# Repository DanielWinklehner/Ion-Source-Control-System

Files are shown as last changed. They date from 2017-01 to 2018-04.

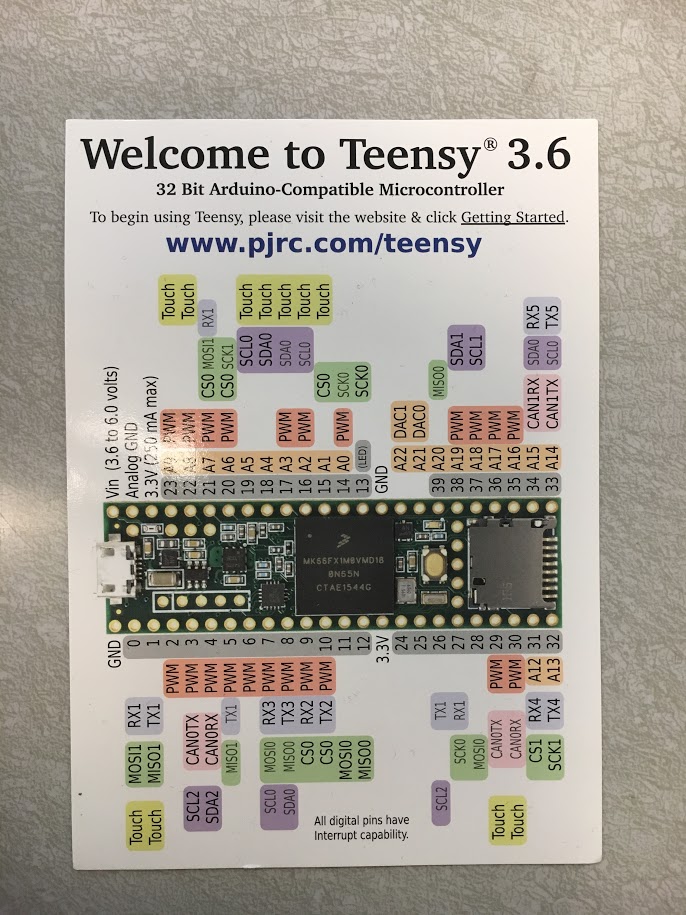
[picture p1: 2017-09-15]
Documents/Manuals/teensy_pinout.JPG

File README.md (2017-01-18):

# Ion Source Control System

## Arduino Error Codes
'ERR0' => Undefined error (does not fall into any of the other 9 categories).
'ERR1' => Asking a precision that's too high (> 6).
'ERR2' => Asking for something that would return more than 128 bytes.
'ERR3' => Invalid number of channels.
'ERR4' => Querying for a channel that does not exist.
'ERR5' => ...
'ERR6' => ...
'ERR7' => ...
...

## Libraries to Install

## Killing the server.

```bash
ps aux | grep RasPiServer.py | grep -v grep | awk '{print $2}' | xargs kill -9 ; python RasPiServer.py 
```

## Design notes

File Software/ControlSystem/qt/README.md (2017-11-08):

# Qt Ion Source Control System Software

Written for Python 3/PyQt5/PyQtGraph

New features:
 - No interruption on device disconnect (requires newest RasPi server)
 - Procedures

Features from the old control system that haven't been implemented:
 - h5 logging

Requirements:
 - Python 3
 - PyQt5
 - PyQtGraph
 - numpy
 - scipy
 - Requests
 - h5py

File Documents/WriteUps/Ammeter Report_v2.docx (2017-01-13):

# Ammeter Report

# Introduction

The main goal of this experiment has been to measure the output signal of a Trans Impedance Amplifier (TIA) wired to a current source. <more information: why are we testing this, what assumptions have you made, what ranges are we interested in? what are all the options for these ranges?>

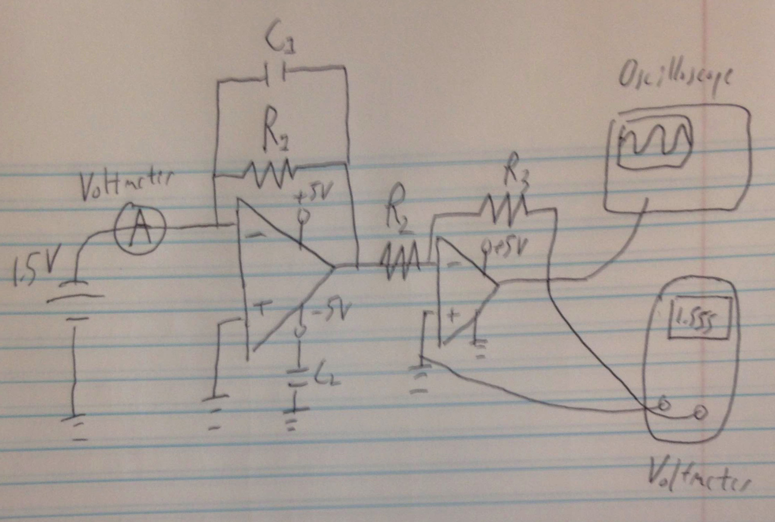
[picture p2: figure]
Macintosh HD:Users:smilner2:Desktop:IMG_0299.pdf

Figure 1: Schematic of the Trans Impedance Amplifier (TIA) with subsequent inverter.

# Setup and Test Cases

The general layout of the circuit is shown in Figure 1.

<restructure and reformat this, explain the parts of the circuit, put all the values in the table instead of the text.>

In this case the current source consisted of a 1.5 V battery connected to a potentiometer that allowed for a wide range of current values. Two different feedback resistors for the TIA were implemented, a 21.9 Ω resistor for a gain 1000 amplifier and a 1.788 k Ω resistor for a gain 10 amplifier. A 1000 μ F feedback capacitor was also incorporated into the TIA as well as another 1000 μ F capacitor which was grounded in order to eliminate noise from the 5V power source.

By conducting measurements using the gain 1000 amplifier it was found that a low feedback resistor corresponds to a very large amount of noise in the range of hundreds of millivolts. Thus it was determined that future measurements using the ammeter should only be done using large feedback resistors with low gain amplification.

Table 1: Resistor and Capacitor values for the different test cases.

Element | Case 1 | Case 2
R1 | 21.9 Ω | 1.788 kΩ
R2
R3
etc….

# Measurements

<brief explanation>

## Case 1

<put everything pertinent to case 1 (21.9 Ohm) here. Table with values, figure, etc.>

## Case 2

<put everything pertinent to case 2 (1.788 kOhm) here. Table with values, figure, etc.>

I(microamps) | V(output) | V(expected) | V(ripple) | Output Error | V(expected)-V(output)
25.6 | 0.549 | 0.553 | 0.002 | 0.00052 | 0.004
31 | 0.662 | 0.67 | 0.0075 | 0.000586 | 0.008
39.5 | 0.848 | 0.865 | 0.01 | 0.000688 | 0.017
46.8 | 1.01 | 1.027 | 0.0066 | 0.000776 | 0.017
53.7 | 1.156 | 1.176 | 0.0056 | 0.000859 | 0.02
67 | 1.465 | 1.467 | 0.0041 | 0.00102 | 0.002
68.3 | 1.472 | 1.475 | 0.0055 | 0.00103 | 0.003
79.8 | 1.722 | 1.724 | 0.0045 | 0.00172 | 0.002
89.4 | 1.933 | 1.931 | 0.0033 | 0.00128 | 0.002
93.1 | 2.013 | 2.011 | 0.0044 | 0.00133 | 0.002
98.5 | 2.126 | 2.128 | 0.0047 | 0.001163 | 0.002
111.1 | 2.401 | 2.399 | 0.0051 | 0.00155 | 0.002
119.9 | 2.599 | 2.59 | 0.0067 | 0.00122 | 0.009
123.9 | 2.683 | 2.676 | 0.0035 | 0.00132 | 0.007
135.6 | 2.918 | 2.929 | 0.013 | 0.00143 | 0.009
148.3 | 3.215 | 3.203 | 0.0088 | 0.00155 | 0.012
158.1 | 3.435 | 3.415 | 0.011 | 0.00176 | 0.03
167.5 | 3.687 | 3.618 | 0.0061 | 0.0019 | 0.069
177.4 | | 3.831 | 0.0072 | 0.0201 | 0
185.6 | | 3.831 | 0.0054 | 0.00222 | 0
196.9 | | 3.831 | 0.003 | 0.00258 | 0

For this case of a 1.785 feedback resistor the data measured included the input current, the output voltage as well as the ripple voltage measured using the oscilloscope. Additional values were the expected output voltage, the difference between expected and output voltages and the error in the expected voltage. The error in the expected voltage was found using Ohm’s law and the intrinsic error in the input current and the resistors. In this case the error in the current was constant at 0.01 μ A and the error in the resistors was also constant at 0.001 k Ω .

After finding the error values for the expected voltage it was possible to add error bars on the graphs in Excel for all the data series that are tabulated above. Using the Custom error option and the Errors data it was possible to add in bars for each data point in the expected output voltage error series.

Table 3. Constant error values

| Output Voltage | Input Current | Resistors
Error | ± 0.01 V | ± 0.01 μA | ± 0.001 k Ω

Figure 4. Table of 21.9 ohm feedback data

I(microamps) | V(ripple) (Volts) | V(Output) (Volts) | V(expected) (Volts) | V(output)-V(expected) (Volts) | Expected Voltage Error
46.9 | 0.23 | 1.416 | 1.027 | 0.389 | 0.000776
68.3 | 0.513 | 1.845 | 1.496 | 0.349 | 0.00111
75.6 | 0.411 | 0.856 | 1.656 | 0.8 | 0.00168
111.6 | 0.354 | 1.999 | 2.444 | 0.445 | 0.00154

# Conclusion

For future work on the ammeter it has been posited that for current values in the 0-200 mA range measuring an output voltage should be done using shunt resistors. The reason for this is due to the high level of noise present in using a low feedback resistor as shown in the data for a 21.9 Ω resistor. For the maximum current of 200 mA in order to achieve a maximum voltage of 3.747 V a shunt resistor of 18.74 Ω should be used which will give a corresponding power of 0.749 W.

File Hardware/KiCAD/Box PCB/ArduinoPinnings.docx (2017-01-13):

Arduino 1

- Solenoid valves
  - Open/closed 1 – 50
  - Open/closed 2 – 52
  - 5v – 46
  - UNUSED – 48 (will flip 4th relay, unconnected)
- Vacuum valves
  - Open 1 – 21
  - Closed 1 – 20
  - Open 2 – 19
  - Closed 2 – 18
- Open LED – 11
- Closed LED – 10
- Error LED – 12
- Com LED – 13

Arduino 2

- Temperature 1
  - SDO – 40
  - SDI – 42
  - SCK – 44
  - CS 1 – 46
  - CS 2 – 48
  - CS 3 – 50
  - CS 4 – 52
- Temperature 2
  - SDO – 53
  - SDI – 51
  - SCK – 49
  - CS 5 – 47
  - CS 6 – 45
  - CS 7 – 43
  - CS 8 – 41
- Flow meters
  - 1 -- 18
  - 2 – 19
  - 3 – 20
  - 4 – 3
  - 5 – 2
- Error LED – 12
- Com LED – 13

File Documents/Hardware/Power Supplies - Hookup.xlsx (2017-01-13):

Label | Volts | Amps | Connect to | Comment
Filament Heating | 200 | 10 | Iso Transformer SEC1
Filament Discharge | 117 | 10 | Iso Transformer SEC2
PLC II | 117 | 1 | Iso Transformer SEC3
Iso Transformer | 208 | 20 | Breaker Box | Breaker Box needs to be made (mushroom shut-off)
Ion Source HV | 240 | 12 | Breaker Box | Runs ok on 208, max 15 A
Einzel Lens HV | 240 | 6 | Breaker Box | Runs ok on 208, max 8 A
Puller | 120 | 5 | Rack Power Strip | Sits in NIM Crate
Turbo Pump Controller | 120 | 8 | Rack Power Strip | 2x
PC | 120 | 5 | Existing Outlets | Nothing to to
PLC I | 120 | 1 | Rack Power Strip
Ion Gauge Controller | 120 | 1 | Rack Power Strip
Interlock Box | 120 | 1 | Rack Power Strip | via extension cord
Roughing Pump | 120 | 8 | Rack Power Strip | via extension cord
Misc | 120 | 5 | Existing Outlets | Nothing to do

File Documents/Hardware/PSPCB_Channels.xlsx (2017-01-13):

For each power supply we will need:
Channel | Value | Description
Remote Voltage Programming | 0-10 V | Arduino supplies 0-10V to remotely set voltage of PS (0-5V mode with jumper)
Remote Current Programming | 0-10 V | Arduino supplies 0-10V to remotely set current of PS (0-5V and 0-100mV modes with jumpers)
Remote Voltage Feedback | 0-10 V | Arduino reads 0-10V to remotely read voltage of PS (0-5V mode with jumper)
Remote Current Feedback | 0-10 V | Arduino reads 0-10V to remotely read current of PS (0-5V mode with jumper)
Remote Current Feedback 2 | 0-100mV | Gets dedicated channel as it will need an op-amp
Close PS Interlock | 0/1 | Closes/opens a contact to allow/inhibit PS output. Maybe a relay?
PS ON/OFF Passive | 0/1 | Closes/opens a contact to switch on/off PS. Maybe a relay?
PS ON/OFF Active | 0/10V | Put Output to HIGH (10V)/LOW (0V) to switch on/off PS
External Interlock Input | 0/1 | Register if an external wire loop is closed or not. Connect to Arduino interrupt.
HV ON/OFF Indicator |  | Active Transistor. Maximum output current is 30mA via an output resistance of 440R
Trip Indicator |  | Active Transistor. Maximum output current is 30mA via an output resistance of 440R
Local/Remote Indicator |  | Active Transistor. Maximum output current is 30mA via an output resistance of 440R
Arc Monitor Status Indicator |  | Active Transistor. Maximum output current is 30mA via an output resistance of 440R
V Status Indicator |  | Active Transistor. Maximum output current is 30mA via an output resistance of 440R
I Status Indicator |  | Active Transistor. Maximum output current is 30mA via an output resistance of 440R
In addition, each arduino gets:
Communicating LED
Error State LED
Reset Button
Highly stable reference voltage
Other ideas?

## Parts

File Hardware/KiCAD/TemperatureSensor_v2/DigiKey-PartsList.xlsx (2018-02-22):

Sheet: First Order
name | part number | qty
100 nF cap | 490-6328-1-ND | 22
10 uF cap | 490-10693-1-ND | 1
diode | 1N4148WXTPMSTR-ND | 6
led | 160-1447-2-ND | 4
zener | BZT52C15-FDITR-ND | 1
fuse holder | F1498-ND | 1
barrel jack | CP-202B-ND | 1
com connector | S7002-ND | 1
3.3k resistor | RR08P3.3KDCT-ND | 6
1k resistor | RR05P1.0KDCT-ND | 4
push button | EG2509-ND | 1
voltage regulator | 497-1491-5-ND | 1

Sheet: Revision
name | part number | qty
100 nF cap | 709-1183-1-ND | 22
10 uF cap | 490-10693-1-ND | 1
diode | 1N4148WXTPMSTR-ND | 6
led | 160-1447-2-ND | 4
zener | BZT52C15S-FDICT-ND | 1
fuse holder | 486-2019-ND | 2
barrel jack | CP-202AH-ND | 1
com connector | S7002-ND | 1
3.3k resistor | P3.3KDBCT-ND | 6
1k resistor | RR08P1.0KDDKR-ND | 4
push button | EG2509-ND | 1
voltage regulator | 497-1491-5-ND | 1
MAX | MAX31856MUD+-ND | 1

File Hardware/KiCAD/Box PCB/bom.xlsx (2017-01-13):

Component | Value | Quantity | size/ref
Capacitor
 | 10uF | 1 | 805 | http://www.mouser.com/ProductDetail/TDK/C2012X7R1A106K125AE/
 | .1uF | 25 | 805 | http://www.mouser.com/ProductDetail/Vishay-Vitramon/VJ0805Y104JXQCW1BC/
 | .01uF | 16 | 805 | http://www.mouser.com/ProductDetail/Vishay-Vitramon/VJ0805Y103JXQCW1BC/
Resistor
 | 1k | 14 | 603 | http://www.mouser.com/ProductDetail/Bourns/CRT0603-BY-1001EAS/
 | 3.3k | 12 | 603 | http://www.mouser.com/ProductDetail/Panasonic/ERA-3AEB332V/
 | 10k | 7 | 603 | http://www.mouser.com/ProductDetail/Bourns/CRT0603-BY-1002EAS/
Diode |  | 10
 | n/a |  | SMD SOD-323 | http://www.mouser.com/ProductDetail/Vishay-Semiconductors/1N4148WS-E3-08/?qs=sGAEpiMZZMtoHjESLttvkjs26zymxl2FcQ6lZ9nzG2I%3d
LED
 | red | 8 | 3mm | http://www.mouser.com/ProductDetail/Kingbright/WP710A10ID/
transistor |  | 2 | SOT-223 | http://www.mouser.com/Search/ProductDetail.aspx?qs=UMEuL5FsraAkzKOnvvq6XA%3d%3d
voltage regulator |  | 1 | SOT-223-3 | http://www.mouser.com/ProductDetail/STMicroelectronics/LD1117S33TR/?qs=edoyzKMbmhntQZx4BFmoqw%3D%3D
Connectors
 | 01x02 | 9
 | 01x07 | 2
 | 01x09 | 1
 | 01x13 | 4
MAX31856
 |  | 8 | 14 pin TSSOP | http://www.mouser.com/ProductDetail/Maxim-Integrated/MAX31856MUD+/
Solder paste
 | Easy 256 from Kester
Solder squeegee

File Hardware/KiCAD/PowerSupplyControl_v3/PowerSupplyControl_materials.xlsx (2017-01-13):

Item | value | Quantity (per board) | Footprint | Link
Diode
 |  | 4 | SOD-323 | http://www.mouser.com/ProductDetail/Vishay-Semiconductors/1N4148WS-E3-08/?qs=sGAEpiMZZMtoHjESLttvkjs26zymxl2FcQ6lZ9nzG2I%3d
Resistors
 | 1k | 42 | 603 | http://www.mouser.com/ProductDetail/Bourns/CRT0603-BY-1001EAS/
 | 1.4k | 4 | 603 | http://www.mouser.com/ProductDetail/Panasonic/ERA-3AEB1401V/
 | 3.3k | 8 | 603 | http://www.mouser.com/ProductDetail/Panasonic/ERA-3AEB332V/?qs=sGAEpiMZZMu61qfTUdNhGxEjuuBLd0B4AgtkKscHp9I%3d
 | 10k | 5 | 603 | http://www.mouser.com/ProductDetail/ARCOL-Ohmite/APC0603B10K0N/
 | 13k | 8 | 603 | http://www.mouser.com/ProductDetail/Susumu/RR0816P-133-D/
 | 20k | 12 | 603 | http://www.mouser.com/ProductDetail/ARCOL-Ohmite/APC0603B20K0N/
 | 487k | 4 | 805 | http://www.mouser.com/ProductDetail/Welwyn-Components-TT-Electronics/PCF0805R-487KBT1/
Capacitors
 | 0.01uF | 4 | 805 | http://www.mouser.com/ProductDetail/Murata-Electronics/GRM2195C1H103FA01D/?qs=sGAEpiMZZMs0AnBnWHyRQG5q9snugj0Qdwer2IwkegU%3d
 | 0.1uF | 9 | 805 | http://www.mouser.com/ProductDetail/Kemet/C0805C104J5RACTU/
 | 1uF | 1 | 805 | http://www.mouser.com/ProductDetail/Kemet/C0805C105J4RACTU/
 | 10uF | 1 | 805 | http://www.mouser.com/ProductDetail/Murata-Electronics/GRM21BR61C106KE15L/?qs=sGAEpiMZZMs0AnBnWHyRQFQYdTDrJniY6UiV3hUxNOg%3d
 | 47uF | 4 | 1210 | http://www.mouser.com/ProductDetail/Murata-Electronics/GRM32EC81C476KE15L/
DIP switches
 |  | 4 |  | http://www.mouser.com/ProductDetail/CK-Components/BD01/?qs=mh%2FGhdZp9qW9ttlbghPYvg%3D%3D
MAX31856
 |  | 2 |  | http://www.mouser.com/ProductDetail/Maxim-Integrated/MAX31856MUD+/
Terminal Blocks
 |  | 3 (2 pole)
 |  | 3 (10 pole)
Double sided headers
 |  | 1 (6 pins) | 2.54mm | http://www.mouser.com/ProductDetail/SchmartBoard/920-0085-01/
 |  | 5 (8 pins) | 2.54mm | http://www.mouser.com/ProductDetail/SchmartBoard/920-0086-01/
 |  | 1 (2x18 pins) | 2.54mm | http://www.mouser.com/ProductDetail/SchmartBoard/920-0103-01/
 |  | ~~(maybe extenders?)~~ | ~~2.54mm~~
Op Amps
 |  | 3 | soic-14 | http://www.mouser.com/ProductDetail/Texas-Instruments/LM324MX-NOPB/
ADR4550
 |  | 1 |  | http://www.mouser.com/ProductDetail/Analog-Devices/ADR4550BRZ/?qs=sGAEpiMZZMv9Q1JI0Mo%2ftYZUeGvTlaqP

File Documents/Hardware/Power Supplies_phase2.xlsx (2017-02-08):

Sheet: Sheet1
Description | Company | Series | Input | Phases | Max Output | Max Power | Iso Transformer | Comment
Filament Current Supply | Electronic Measurements, Inc. | TCR | 190-250 VAC | 1 | 10 VDC, 300 A | 1.2 kW | SEC1 | Not going to exceed 100 A, Set PLC upper limit.
Filament Discharge Supply | Power Ten, Inc. | 3300P | 120 VAC | 1 | 100 VDC, 10A | 1.2 kW | SEC2
PLC II | MIT | - | 120 VAC | 1 | - | 500 W | SEC3 | PLC II for everything on HV potential
Isolation Transformer | Stewart Transformers, London | STL | 208 VAC | 1 | - | 4 kVA | PRY | See Plaque for Output, 60 kV isolation
HV Power Supply | Farnell Hivolt | 2500 | 240 VAC | 1 | 20 kV, 120 mA | 2.9 kW | N/A | Runs OK on 208 VAC
Einzel Lens Power Supply | Glassman High Voltage, Inc. | WX | 240 VAC | 1 | 30 kV, 40 mA | 1.4 kW | N/A | 2 phases from 120/208 VAC?
Extraction, Negative PS | TBD | TBD | 120 VAC | 1 | 5 kV, 40 mA | 300 W | N/A | Need to buy this, necessary in MIST-1/Phase II
Turbo Pump Controller | ? | ? | 120 VAC | 1 | - | ? | N/A | Will eventually run 2 of them
PC | - | - | 120 VAC | 1 | - | 500 W | N/A
PLC I | MIT | - | 120 VAC | 1 | - | 500 W | N/A | PLC I for everything not on HV potential
Ion Gauge Controller | MIT | - | 120 VAC | 1 | - | 150 W | N/A
Misc | MIT | - | 120 VAC | 1 | - | 1 kW | N/A | Other diagnostic devices, not to exceed 1 kW
On HV Potential
Iso Transformer
On Ground Potential

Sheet: Sheet2
Label | Volts | Amps | Connect to | Comment
Filament Heating | 200 | 10 | Iso Transformer SEC1
Filament Discharge | 117 | 10 | Iso Transformer SEC2
PLC II | 117 | 1 | Iso Transformer SEC3
Iso Transformer | 208 | 20 | Breaker Box | Breaker Box needs to be made (mushroom shut-off)
Ion Source HV | 240 | 12 | Breaker Box | Runs ok on 208
Einzel Lens HV | 240 | 6 | Breaker Box | Runs ok on 208
Puller | 120 | 5 | Rack Power Strip | Sits in NIM Crate
Turbo Pump Controller | 120 | 8 | Rack Power Strip | 2x
PC | 120 | 5 | Existing Outlets | Nothing to to
PLC I | 120 | 1 | Rack Power Strip
Ion Gauge Controller | 120 | 1 | Rack Power Strip
Interlock Box | 120 | 1 | Rack Power Strip
Misc | 120 | 5 | Existing Outlets | Nothing to do
Dipole PS | 120 | 20
Quad PS | 120 | 20 |  | 2x
Lines: |  |  |  |  | Watts
1 | 208 | 20 | to Transformer | shunt-tripped | 4160
2 | 208 | 16 | to HV 1 | shunt-tripped | 3328
3 | 208 | 16 | to HV 2 | shunt-tripped | 3328
4 | 120 | 16 | Rack Strip 1 | shunt-tripped | 1920
5 | 120 | 16 | Rack Strip 2 |  | 1920
6 | 120 | 20 | Dipole PS |  | 2400
7 | 120 | 20 | Quad PS 1 |  | 2400
8 | 120 | 20 | Quad PS 2 |  | 2400
9 | 120 | 16 | Misc 1 | Existing wall strips | 1920
10 | 120 | 16 | Misc 2 | Existing wall strips | 1920
 |  |  |  |  | 25.7 | kW

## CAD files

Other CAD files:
Hardware/KiCAD/TemperatureSensor/inventor/temp_sensor_front_plate.dwg
Hardware/KiCAD/TemperatureSensor/inventor/temp_sensor_back_plate.ipt
Hardware/KiCAD/TemperatureSensor/inventor/temp_sensor_front_plate.ipt

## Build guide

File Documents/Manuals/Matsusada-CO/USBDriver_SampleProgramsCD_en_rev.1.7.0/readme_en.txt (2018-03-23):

====================================================================================================
[Software ]		USB Driver / Sample Programs
[ Version ]		Ver.1.7.0
[Copyright]		2016(c) Matsusada Precision Inc, All rights reserved.
[  U R L  ]		www.matsusada.com/
====================================================================================================

1. About "USB Driver / Sample Programs"
	"USB Driver / Sample Programs" contains drivers, manuals and sample programs to control
	the USB devices made by Matsusada Precision Inc.
	You should install this driver in the operating environment to control the USB devices
	made by Matsusada Precision Inc. remotely.

2. Directory Structure
	"USBDriver_SamplePrograms"
		„° "readme_en.txt"
		„° "Documents"
		„«		„° "CDM 2 08 28 Release Info.rtf"			�F	Driver Rev.2.08.28 Release Info
		„«		„° "D2XX_Programmer's_Guide(FT_000071).pdf"	�F	Device Driver Programmer's Guide (English)
		„«		„° "LogoVerificationReport.pdf"				�F	Windows Certification Report
		„«		„¯ "USBDriverInstallationGuide_en_rev.1.3.pdf"	�F	USB Driver Installation Guide (English)
		„° "Drivers"										�F	Device Driver Set
		„¯ "Sample Programs"
				„° "LabVIEW"								�F	Sample Program for LabVIEW
				„° "VB"										�F	Sample Program for VB
				„° "VC#"									�F	Sample Program for VC#
				„° "VC++"									�F	Sample Program for VC++
				„¯ "Matsusada_USB_Check.exe"				�F	Communication Check Program

3. Corresponded OS
	Windows 10(32/64bit)(*), 8.1(32/64bit)(*), 8(32/64bit), 7(32/64bit), VISTA(32/64bit), XP(32/64bit)(**)
	(*)	It does not officially get certified with Windows 10 and 8.1 by Microsoft Inc,
		but it was confirmed the operation at Matsusada Precision Inc.
	(**)Operation on Windows XP has been confirmed by us.
		But we preclude any possibility of support for operation on Windows XP, as Support
		for it by Microsoft is terminated.

4. Driver Installation
	Refer to attached "USBDriverInstallationGuide_en_rev.1.3.pdf", install the driver.

5. Exemption Clause
	We are not responsible at all for any trouble or damage, even if such a trouble or damage
	should have happened about your PC, peripheral units, and/or data.  You are requested to
	understand this clause before using the software.

6. Copyright
	The copyright related to this software is possessed by Matsusada Precision Inc.

[EOF]

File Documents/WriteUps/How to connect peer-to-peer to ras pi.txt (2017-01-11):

The Raspberry Pi needs to have a static IP set on it. For this document, let's assume it's 10.77.0.3

On your computer:

1) Disable WiFi
2) Set up static IP for your computer as well. Set it to: 10.77.0.1. Set the netmask to 255.255.0.0 and the gateway to 10.77.0.1 (or whatever static IP you have set your computer's address to).
3) Ping the IP of the Pi to see if it responds.
4) SSH.

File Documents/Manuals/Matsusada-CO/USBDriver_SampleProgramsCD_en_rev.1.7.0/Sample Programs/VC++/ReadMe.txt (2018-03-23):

========================================================================
    アプリケーション: Matsusada_USB_Sample プロジェクトの概要
========================================================================

この Matsusada_USB_Sample アプリケーションは、AppWizard により作成されました。  

このファイルには、Matsusada_USB_Sample 
アプリケーションを構成する各ファイルの内容の概要が含まれています。

Matsusada_USB_Sample_Cpp.vcxproj
    これは、アプリケーション ウィザードを使用して生成された VC++ 
    プロジェクトのメイン プロジェクト ファイルです。 
    ファイルを生成した Visual C++ のバージョンに関する情報と、アプリケーション 
    ウィザードで選択されたプラットフォーム、
    構成、およびプロジェクト機能に関する情報が含まれています。

Matsusada_USB_Sample_Cpp.vcxproj.filters
    これは、アプリケーション ウィザードで生成された VC++ プロジェクトのフィルター 
    ファイルです。 
    このファイルには、プロジェクト内のファイルとフィルターとの間の関連付けに関する
    情報が含まれています。 
    この関連付けは、特定のノードで同様の拡張子を持つファイルのグループ化を
    示すために IDE で使用されます (たとえば、".cpp" ファイルは "ソース ファイル" 
    フィルターに関連付けられています)。

Matsusada_USB_Sample.cpp
    これは、メインのアプリケーション ソース ファイルです。
    フォームを表示するコードが含まれています。

Matsusada_USB_Sample.h
    フォーム クラスと InitializeComponent() 関数の実装が含まれています。

AssemblyInfo.cpp
    アセンブリ メタデータを変更するカスタム属性が含まれています。

/////////////////////////////////////////////////////////////////////////////
その他の標準ファイル :

StdAfx.h、StdAfx.cpp
    これらのファイルは、Matsusada_USB_Sample_Cpp.pch 
    という名前のプリコンパイル済みヘッダー (PCH) ファイルと、StdAfx.obj 
    という名前のプリコンパイル済みの型ファイルを構築するために使用されます。

/////////////////////////////////////////////////////////////////////////////

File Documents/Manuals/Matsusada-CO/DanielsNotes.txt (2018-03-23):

1. Manually install d2xx drivers on RasPi. Has to be version 1.3.x (or maybe just have to sudo).
Link: http://www.ftdichip.com/Drivers/D2XX.htm (use the v6 that says works on RasPi, follow instructions in readme in the rightmost column)
(CO-U32 serial number is CO001144)
2. If you compile the tests/examples, there is a small modification necessary in the loopback example 
(just add "../" in front of the import statement in main.c)
3. Install ftd2xx from https://github.com/ctrl-shift-esc/ftd2xx (has Linux version as opposed to PyUSB 1.6)
4. Compile ftd2xx as sudo! (sudo python setup.py install)

5. Run python as sudo, test the comunication:

BaudRate 9600, 8 data bits, 1 stop bit, no parity, no flow control
500 ms read, 100 ms write timeout (in Matsusada Example Code)

import ftd2xx

ftd2xx.setVIDPID(0x1192, 0x1000)  # Add our devices Vendor ID and Product ID to the loaded list of FTDI ID's
dev = ftd2xx.open(0)  # if there is only one FTDI device connected or CO happens to be the first one in the list, otherwise, different index
dev.setBaudRate(9600)
dev.setDataCharacteristics(8, 0, 0)  # 8 data bits, 1 stop bit (for some reason BITS_8 = 0), parity none = 0
dev.setFlowControl(0x0000)
dev.write("#1 REN\r")  # needs a carriage return, not a newline! #1 can be replaced with units 2, 3, 4, etc.

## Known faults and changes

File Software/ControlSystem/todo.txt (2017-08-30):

Procedures

 - User can define procedures, with access to channels
    e.g. "if channel goes over this value, do X"
 - Idea: Drop down combobox w/ channels, put in max/min values
 - Idea: Pop up screen with active channels and variable names, example script, user writes simple if statements

Error Handling

 - Between raspberry pi and gui, between raspberry pi and devices
    currently sends back ERR[0-9]
 - Timeouts between GUI and raspberry pi, if arduino goes offline
    Displaying polling rate in GUI, falls back to polling rate of slowest arduino

General

 - Front page overview, can set overview present when channel is created
 - Decide which panels we want on the front page, currently everything is on the front page
 - Python3 ready
 - Move to QT?

USB

 - Driver for new power supply

Arduino

 - Arduino IDE installed, go to libraries folder, create a folder for the communications library
    Create a symlink to libraries folder
 - Test Arduino using serial plotter from Arduino IDE
 - Has a function for querying value of specific channel, and listing channels available
    sends 'i' or 'c', sends back list of channel names, use to determine which channels to fill

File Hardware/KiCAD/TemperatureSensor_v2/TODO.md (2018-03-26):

# Temperature Sensor (v2) Todo Items

Author: Thomas Wester

Email: twester@mit.edu

Date: 2018/03/06

 - The Arduino footprint is slightly too wide. This
   should be narrowed by ~0.5 mm.

 - Test pads should be added around each MAX controller
   and probably the voltage regulator.

 - The labelling can be improved. The capacitors and MAXs
   have difficult-to-follow numberings. The SDO pin is
   missing a label.

 - The thermocouple footprint pads are too close together.
   These should be extended by ~0.5mm.

 - The solder pads for the thermocouple connectors are too
   small. These should be extended by ~0.5mm.

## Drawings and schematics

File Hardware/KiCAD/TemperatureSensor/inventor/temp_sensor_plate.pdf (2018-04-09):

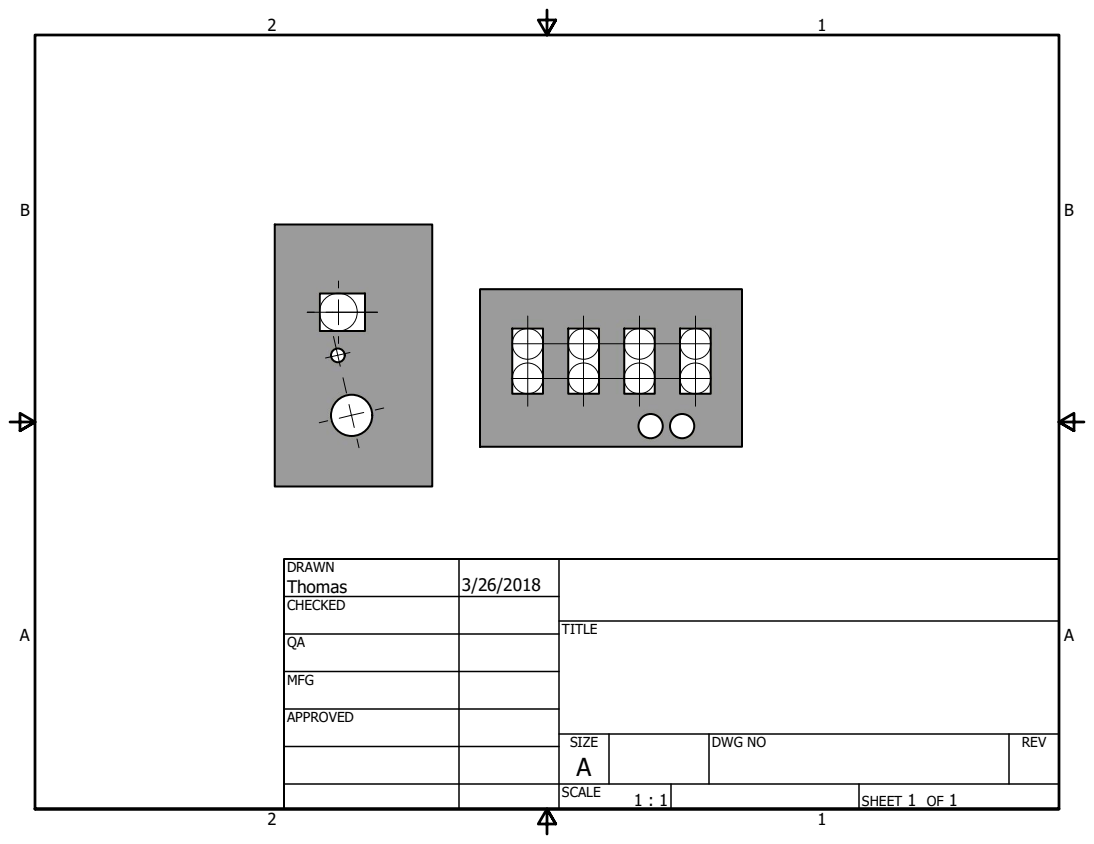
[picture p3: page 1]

DRAWN Thomas | 3/26/2018

CHECKED

MFG

APPROVED

SIZE A | DWG NO | REV

SCALE 1 : 1 | | SHEET 1 OF 1

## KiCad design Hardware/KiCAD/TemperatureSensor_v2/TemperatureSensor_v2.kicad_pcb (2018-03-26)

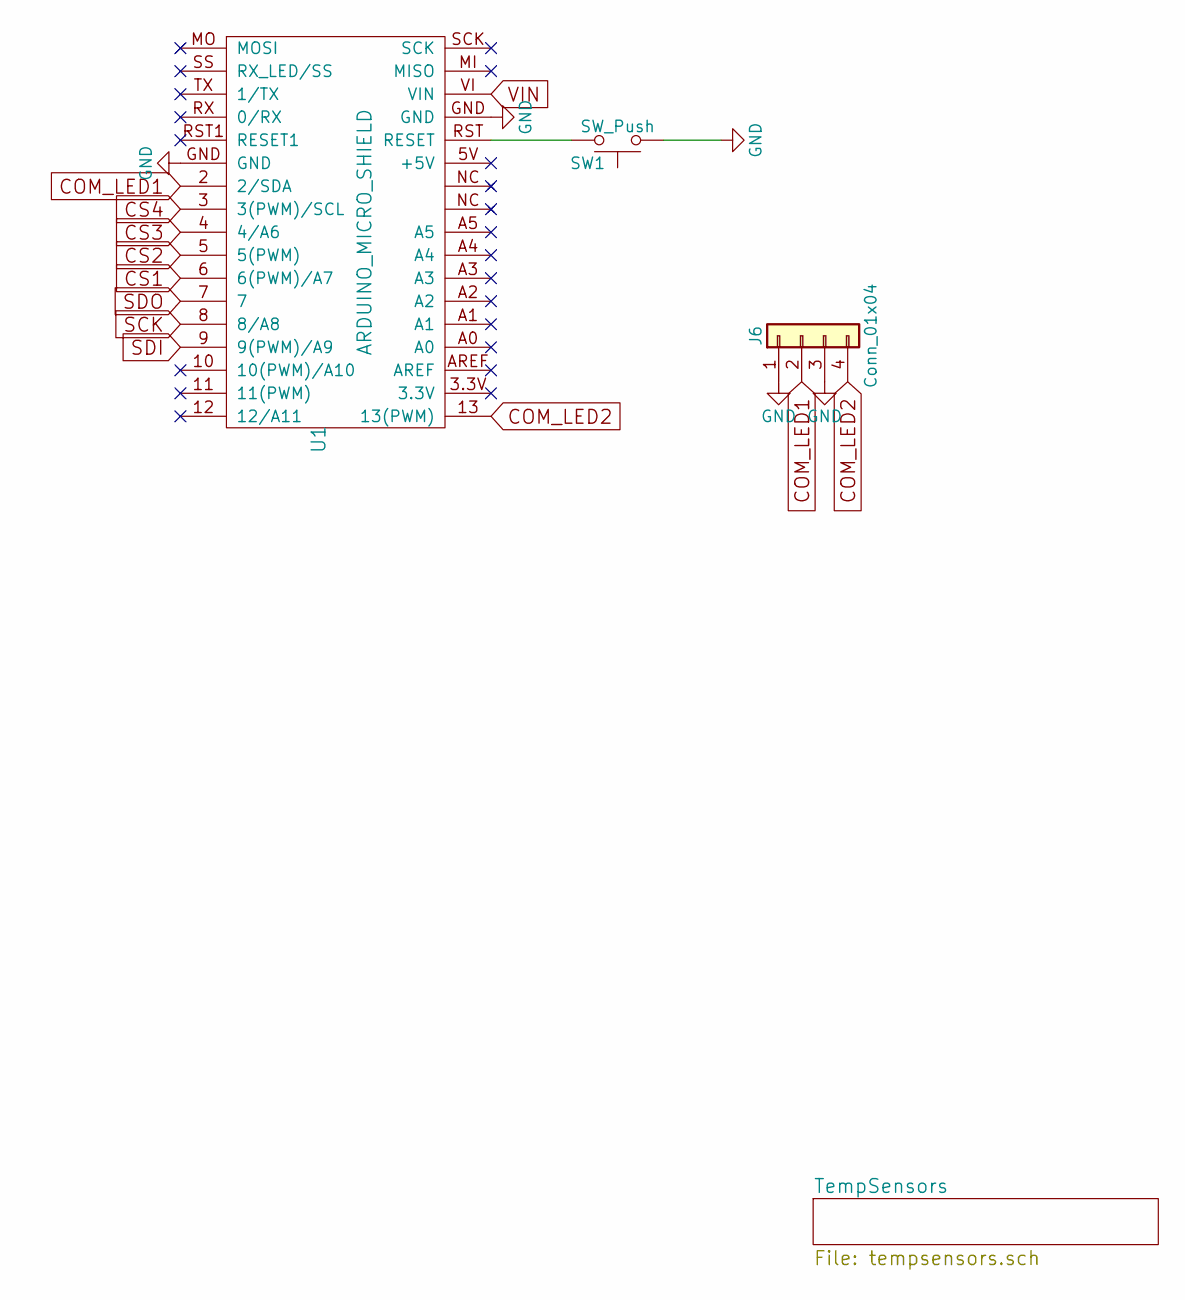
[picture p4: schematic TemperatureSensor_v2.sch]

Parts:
J6: Conn_01x04; TerminalBlock_Phoenix_MPT-2.54mm_4pol
SW1: SW_Push; SW_Tactile_SPST_Angled_PTS645Vx39-2LFS
U1: ARDUINO_MICRO_SHIELD; ARDUINO_MICRO_SHIELD1

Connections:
COM_LED1: J6.2, U1.2 (2/SDA)
COM_LED2: J6.4, U1.13 (13(PWM))
CS1: U1.6 (6(PWM)/A7); also elsewhere on the board
CS2: U1.5 (5(PWM)); also elsewhere on the board
CS3: U1.4 (4/A6); also elsewhere on the board
CS4: U1.3 (3(PWM)/SCL); also elsewhere on the board
GND: J6.1, J6.3, SW1.1, U1.GND; also elsewhere on the board
unnamed: SW1.2, U1.RST (RESET)
SCK: U1.8 (8/A8); also elsewhere on the board
SDI: U1.9 (9(PWM)/A9); also elsewhere on the board
SDO: U1.7; also elsewhere on the board
VIN: U1.VI (VIN); also elsewhere on the board

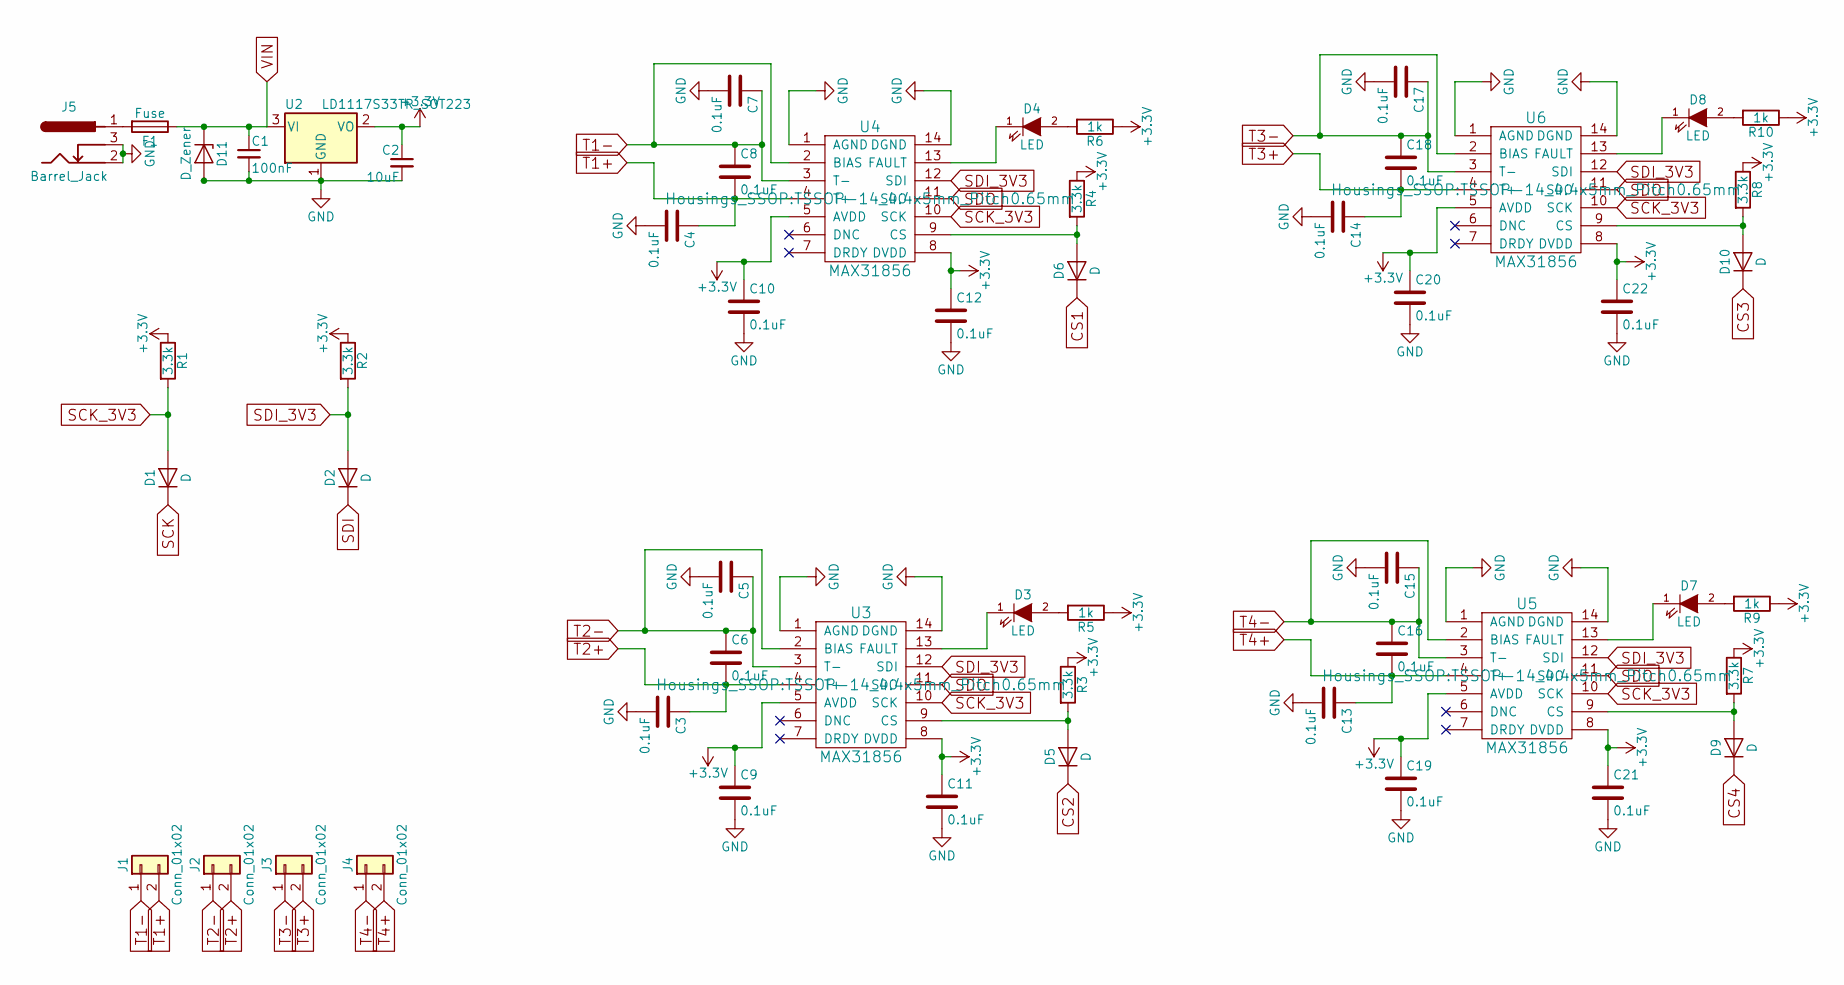
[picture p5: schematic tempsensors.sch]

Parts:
C1: 100nF; C_0805
C2: 10uF; C_0805
C3, C4, C5, C6, C7, C8, C9, C10, C11, C12, C13, C14, C15, C16, C17, C18, C19, C20, C21, C22: 0.1uF; C_0805
D1, D2, D5, D6, D9, D10: D; D_SOD-323
D3, D4, D7, D8: LED; LED_0603
D11: D_Zener; D_0805
F1: Fuse; Fuseholder5x20_horiz_open_inline_Type-I
J1, J2, J3, J4: Conn_01x02; Thermocouple_Pins
J5: Barrel_Jack; BARREL_JACK
R1, R2, R3, R4, R7, R8: 3.3k; R_0603
R5, R6, R9, R10: 1k; R_0603
U2: LD1117S33TR_SOT223; TO-220-3_Vertical
U3, U4, U5, U6: MAX31856; TSSOP-14_4.4x5mm_Pitch0.65mm

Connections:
+3V3: C2.1, C9.1, C10.1, C11.1, C12.1, C19.1, C20.1, C21.1, C22.1, R1.1, R2.1, R3.1, R4.1, R5.1, R6.1, R7.1, R8.1, R9.1, R10.1, U2.2 (VO), U3.5 (AVDD), U3.8 (DVDD), U4.5 (AVDD), U4.8 (DVDD), U5.5 (AVDD), U5.8 (DVDD), U6.5 (AVDD), U6.8 (DVDD)
CS1: D6.1 (K); also elsewhere on the board
CS2: D5.1 (K); also elsewhere on the board
CS3: D10.1 (K); also elsewhere on the board
CS4: D9.1 (K); also elsewhere on the board
GND: C1.2, C2.2, C3.2, C4.2, C5.2, C7.2, C9.2, C10.2, C11.2, C12.2, C13.2, C14.2, C15.2, C17.2, C19.2, C20.2, C21.2, C22.2, D11.2 (A), J5.2, J5.3, U2.1 (GND), U3.1 (AGND), U3.14 (DGND), U4.1 (AGND), U4.14 (DGND), U5.1 (AGND), U5.14 (DGND), U6.1 (AGND), U6.14 (DGND); also elsewhere on the board
unnamed: D3.1 (K), U3.13 (FAULT)
unnamed: D3.2 (A), R5.2
unnamed: D4.1 (K), U4.13 (FAULT)
unnamed: D4.2 (A), R6.2
unnamed: D5.2 (A), R3.2, U3.9 (CS)
unnamed: D6.2 (A), R4.2, U4.9 (CS)
unnamed: D7.1 (K), U5.13 (FAULT)
unnamed: D7.2 (A), R9.2
unnamed: D8.1 (K), U6.13 (FAULT)
unnamed: D8.2 (A), R10.2
unnamed: D9.2 (A), R7.2, U5.9 (CS)
unnamed: D10.2 (A), R8.2, U6.9 (CS)
unnamed: F1.2, J5.1
SCK: D1.1 (K); also elsewhere on the board
SCK_3V3: D1.2 (A), R1.2, U3.10 (SCK), U4.10 (SCK), U5.10 (SCK), U6.10 (SCK)
SDI: D2.1 (K); also elsewhere on the board
SDI_3V3: D2.2 (A), R2.2, U3.12 (SDI), U4.12 (SDI), U5.12 (SDI), U6.12 (SDI)
SDO: U3.11 (SDO), U4.11 (SDO), U5.11 (SDO), U6.11 (SDO); also elsewhere on the board
T1+: C4.1, C8.2, J1.2, U4.4 (T+)
T1-: C7.1, C8.1, J1.1, U4.2 (BIAS), U4.3 (T-)
T2+: C3.1, C6.2, J2.2, U3.4 (T+)
T2-: C5.1, C6.1, J2.1, U3.2 (BIAS), U3.3 (T-)
T3+: C14.1, C18.2, J3.2, U6.4 (T+)
T3-: C17.1, C18.1, J3.1, U6.2 (BIAS), U6.3 (T-)
T4+: C13.1, C16.2, J4.2, U5.4 (T+)
T4-: C15.1, C16.1, J4.1, U5.2 (BIAS), U5.3 (T-)
VIN: C1.1, D11.1 (K), F1.1, U2.3 (VI); also elsewhere on the board

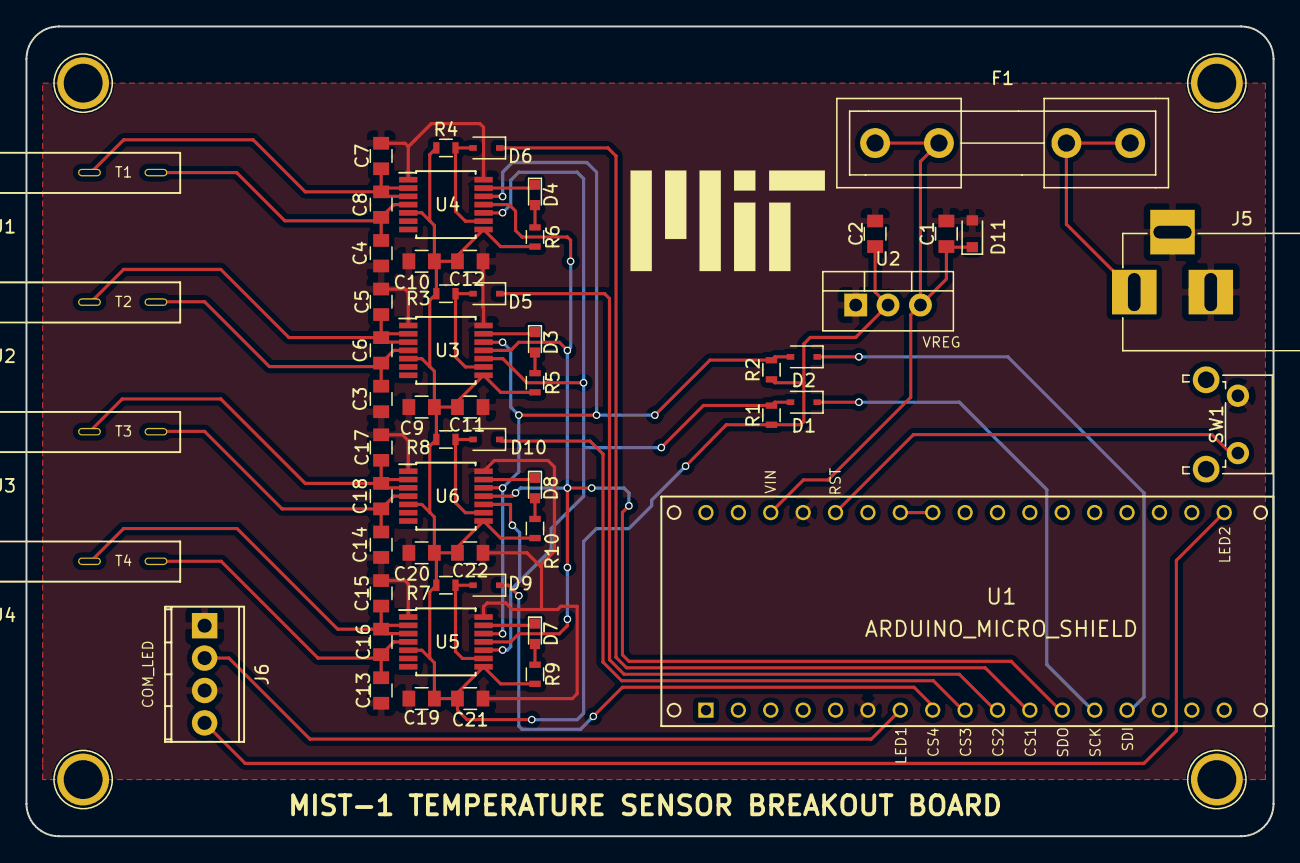
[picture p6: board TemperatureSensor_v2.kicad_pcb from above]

Board: 2 copper layers, 97.8 x 63.5 mm, 57 parts (0 on the bottom side), 36 nets.

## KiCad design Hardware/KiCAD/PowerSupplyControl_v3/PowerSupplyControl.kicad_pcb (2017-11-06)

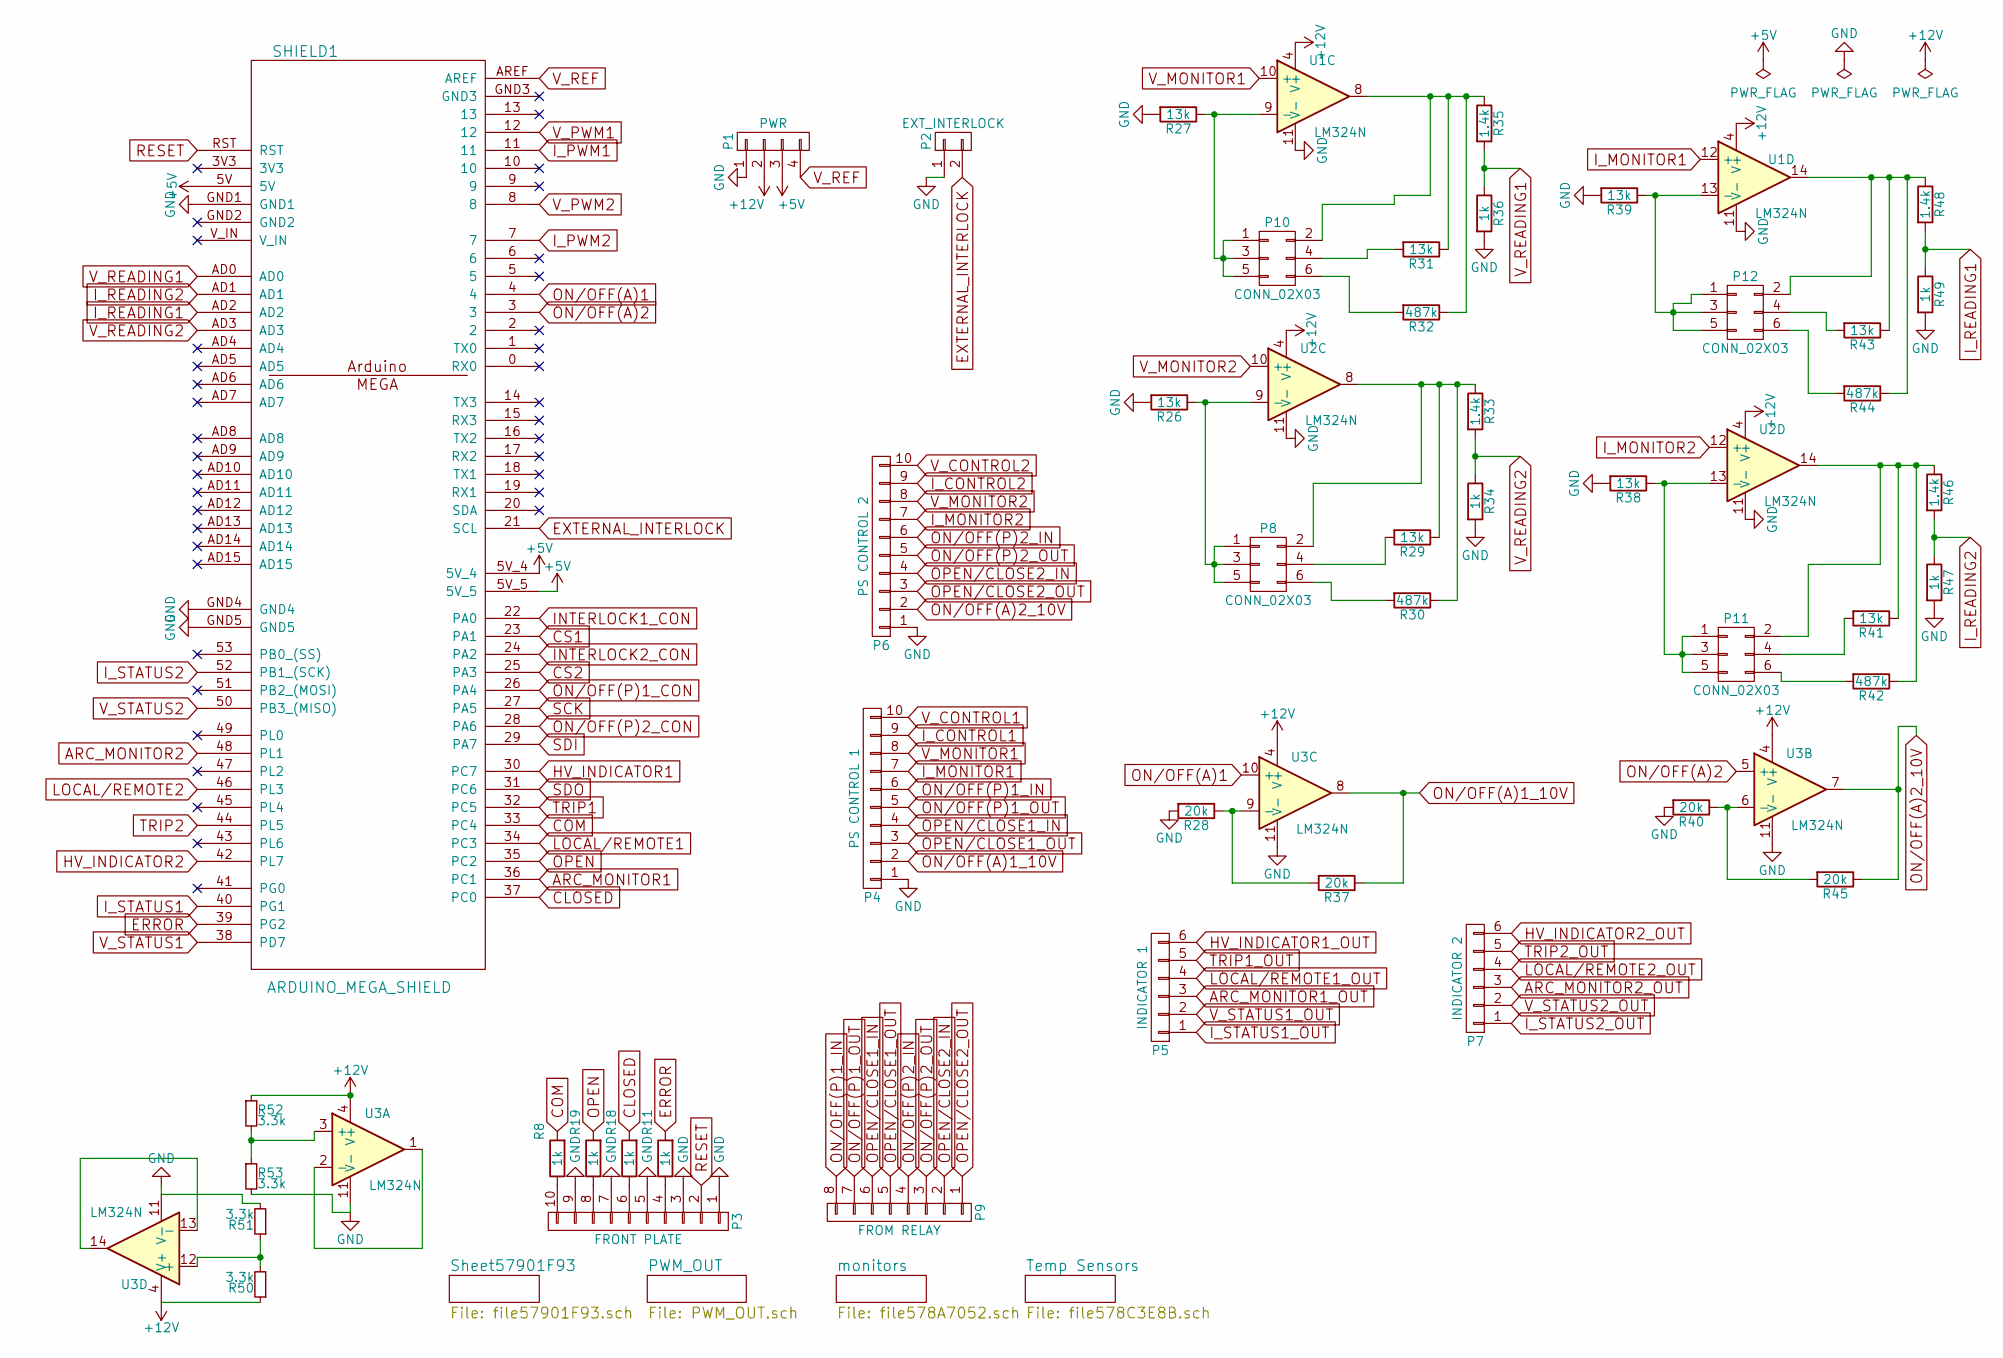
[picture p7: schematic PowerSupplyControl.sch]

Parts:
P1: PWR; Pin_Header_Straight_1x04
P2: EXT_INTERLOCK; TerminalBlock_Pheonix_PT-3.5mm_2pol
P3: FRONT PLATE; TerminalBlock_Pheonix_PT-3.5mm_10pol
P4: PS CONTROL 1; TerminalBlock_Pheonix_PT-3.5mm_10pol
P5: INDICATOR 1; Pin_Header_Straight_1x06
P6: PS CONTROL 2; TerminalBlock_Pheonix_PT-3.5mm_10pol
P7: INDICATOR 2; Pin_Header_Straight_1x06
P8, P10, P11, P12: CONN_02X03; Pin_Header_Straight_2x03
P9: FROM RELAY; Pin_Header_Straight_1x08
R8, R11, R18, R19, R34, R36, R47, R49: 1k; R_0603
R26, R27, R29, R31, R38, R39, R41, R43: 13k; R_0603
R28, R37, R40, R45: 20k; R_0603
R30, R32, R42, R44: 487k; R_0805
R33, R35, R46, R48: 1.4k; R_0603
R50, R51, R52, R53: 3.3k; R_0603
SHIELD1: ARDUINO_MEGA_SHIELD
U1, U2, U3: LM324N; SOIC-14_N

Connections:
+5V: P1.3, SHIELD1.5V, SHIELD1.5V_4, SHIELD1.5V_5; also elsewhere on the board
+12V: P1.2, R50.1, R52.1, U1.4 (V+), U2.4 (V+), U3.4 (V+)
ARC_MONITOR1: SHIELD1.36 (PC1); also elsewhere on the board
ARC_MONITOR1_OUT: P5.3; also elsewhere on the board
ARC_MONITOR2: SHIELD1.48 (PL1); also elsewhere on the board
ARC_MONITOR2_OUT: P7.3; also elsewhere on the board
CLOSED: R18.2, SHIELD1.37 (PC0)
COM: R8.2, SHIELD1.33 (PC4)
CS1: SHIELD1.23 (PA1); also elsewhere on the board
CS2: SHIELD1.25 (PA3); also elsewhere on the board
ERROR: R11.2, SHIELD1.39 (PG2)
EXTERNAL_INTERLOCK: P2.2, SHIELD1.21 (SCL)
GND: P1.1, P2.1, P3.1, P3.3, P3.5, P3.7, P3.9, P4.1, P6.1, R26.2, R27.2, R28.2, R34.2, R36.2, R38.2, R39.2, R40.2, R47.2, R49.2, R51.2, R53.2, SHIELD1.GND1, SHIELD1.GND4, SHIELD1.GND5, U1.11 (V-), U2.11 (V-), U3.11 (V-); also elsewhere on the board
HV_INDICATOR1: SHIELD1.30 (PC7); also elsewhere on the board
HV_INDICATOR1_OUT: P5.6; also elsewhere on the board
HV_INDICATOR2: SHIELD1.42 (PL7); also elsewhere on the board
HV_INDICATOR2_OUT: P7.6; also elsewhere on the board
INTERLOCK1_CON: SHIELD1.22 (PA0)
INTERLOCK2_CON: SHIELD1.24 (PA2)
I_CONTROL1: P4.9; also elsewhere on the board
I_CONTROL2: P6.9; also elsewhere on the board
I_MONITOR1: P4.7, U1.12 (+)
I_MONITOR2: P6.7, U2.12 (+)
I_PWM1: SHIELD1.11; also elsewhere on the board
I_PWM2: SHIELD1.7; also elsewhere on the board
I_READING1: R48.2, R49.1, SHIELD1.AD2
I_READING2: R46.2, R47.1, SHIELD1.AD1
I_STATUS1: SHIELD1.40 (PG1); also elsewhere on the board
I_STATUS1_OUT: P5.1; also elsewhere on the board
I_STATUS2: SHIELD1.52 (PB1_(SCK)); also elsewhere on the board
I_STATUS2_OUT: P7.1; also elsewhere on the board
LOCAL/REMOTE1: SHIELD1.34 (PC3); also elsewhere on the board
LOCAL/REMOTE1_OUT: P5.4; also elsewhere on the board
LOCAL/REMOTE2: SHIELD1.46 (PL3); also elsewhere on the board
LOCAL/REMOTE2_OUT: P7.4; also elsewhere on the board
unnamed: P3.4, R11.1
unnamed: P3.6, R18.1
unnamed: P3.8, R19.1
unnamed: P3.10, R8.1
unnamed: P8.1, P8.3, P8.5, R26.1, U2.9 (-)
unnamed: P8.2, R29.1, R30.1, R33.1, U2.8
unnamed: P8.4, R29.2
unnamed: P8.6, R30.2
unnamed: P10.1, P10.3, P10.5, R27.1, U1.9 (-)
unnamed: P10.2, R31.1, R32.1, R35.1, U1.8
unnamed: P10.4, R31.2
unnamed: P10.6, R32.2
unnamed: P11.1, P11.3, P11.5, R38.1, U2.13 (-)
unnamed: P11.2, R41.1, R42.1, R46.1, U2.14
unnamed: P11.4, R41.2
unnamed: P11.6, R42.2
unnamed: P12.1, P12.3, P12.5, R39.1, U1.13 (-)
unnamed: P12.2, R43.1, R44.1, R48.1, U1.14
unnamed: P12.4, R43.2
unnamed: P12.6, R44.2
unnamed: R28.1, R37.2, U3.9 (-)
unnamed: R40.1, R45.2, U3.6 (-)
unnamed: R50.2, R51.1, U3.12 (+)
unnamed: R52.2, R53.1, U3.3 (+)
unnamed: U3.1, U3.2 (-)
unnamed: U3.13 (-), U3.14
ON/OFF(A)1: SHIELD1.4, U3.10 (+)
ON/OFF(A)1_10V: P4.2, R37.1, U3.8
ON/OFF(A)2: SHIELD1.3, U3.5 (+)
ON/OFF(A)2_10V: P6.2, R45.1, U3.7
ON/OFF(P)1_CON: SHIELD1.26 (PA4)
ON/OFF(P)1_IN: P4.6, P9.8
ON/OFF(P)1_OUT: P4.5, P9.7
ON/OFF(P)2_CON: SHIELD1.28 (PA6)
ON/OFF(P)2_IN: P6.6, P9.4
ON/OFF(P)2_OUT: P6.5, P9.3
OPEN: R19.2, SHIELD1.35 (PC2)
OPEN/CLOSE1_IN: P4.4, P9.6
OPEN/CLOSE1_OUT: P4.3, P9.5
OPEN/CLOSE2_IN: P6.4, P9.2
OPEN/CLOSE2_OUT: P6.3, P9.1
RESET: P3.2, SHIELD1.RST
SCK: SHIELD1.27 (PA5); also elsewhere on the board
SDI: SHIELD1.29 (PA7); also elsewhere on the board
SDO: SHIELD1.31 (PC6); also elsewhere on the board
TRIP1: SHIELD1.32 (PC5); also elsewhere on the board
TRIP1_OUT: P5.5; also elsewhere on the board
TRIP2: SHIELD1.44 (PL5); also elsewhere on the board
TRIP2_OUT: P7.5; also elsewhere on the board
V_CONTROL1: P4.10; also elsewhere on the board
V_CONTROL2: P6.10; also elsewhere on the board
V_MONITOR1: P4.8, U1.10 (+)
V_MONITOR2: P6.8, U2.10 (+)
V_PWM1: SHIELD1.12; also elsewhere on the board
V_PWM2: SHIELD1.8; also elsewhere on the board
V_READING1: R35.2, R36.1, SHIELD1.AD0
V_READING2: R33.2, R34.1, SHIELD1.AD3
V_REF: P1.4, SHIELD1.AREF; also elsewhere on the board
V_STATUS1: SHIELD1.38 (PD7); also elsewhere on the board
V_STATUS1_OUT: P5.2; also elsewhere on the board
V_STATUS2: SHIELD1.50 (PB3_(MISO)); also elsewhere on the board
V_STATUS2_OUT: P7.2; also elsewhere on the board

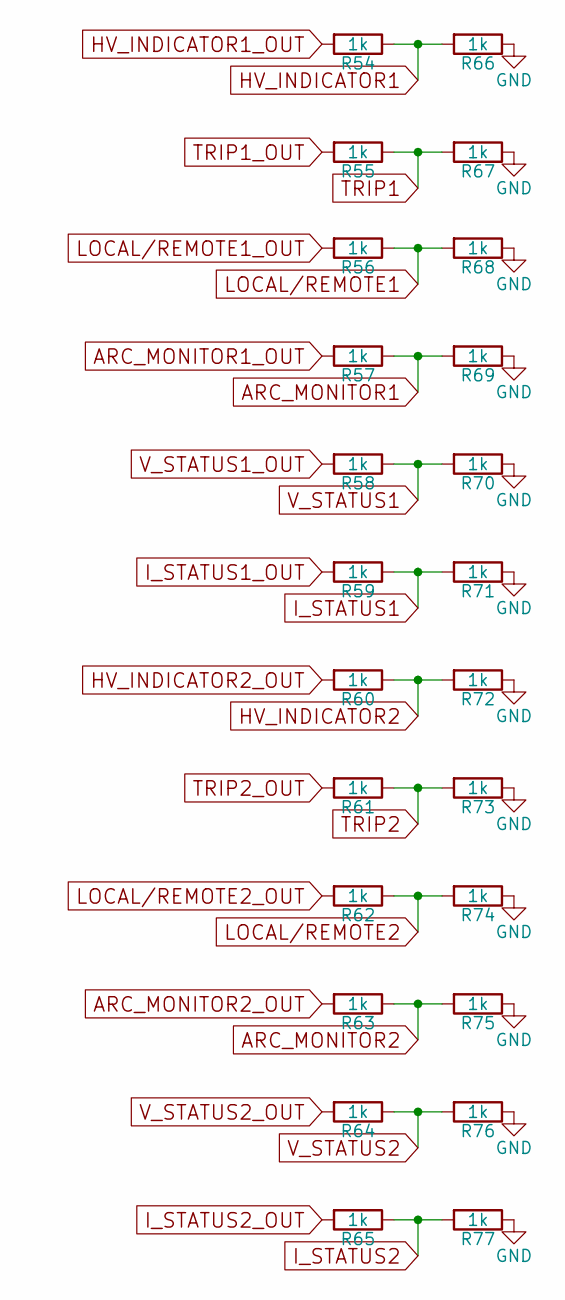
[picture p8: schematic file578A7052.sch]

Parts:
R54, R55, R56, R57, R58, R59, R60, R61, R62, R63, R64, R65, R66, R67, R68, R69, R70, R71, R72, R73, R74, R75, R76, R77: 1k; R_0603

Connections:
ARC_MONITOR1: R57.1, R69.2; also elsewhere on the board
ARC_MONITOR1_OUT: R57.2; also elsewhere on the board
ARC_MONITOR2: R63.1, R75.2; also elsewhere on the board
ARC_MONITOR2_OUT: R63.2; also elsewhere on the board
GND: R66.1, R67.1, R68.1, R69.1, R70.1, R71.1, R72.1, R73.1, R74.1, R75.1, R76.1, R77.1; also elsewhere on the board
HV_INDICATOR1: R54.1, R66.2; also elsewhere on the board
HV_INDICATOR1_OUT: R54.2; also elsewhere on the board
HV_INDICATOR2: R60.1, R72.2; also elsewhere on the board
HV_INDICATOR2_OUT: R60.2; also elsewhere on the board
I_STATUS1: R59.1, R71.2; also elsewhere on the board
I_STATUS1_OUT: R59.2; also elsewhere on the board
I_STATUS2: R65.1, R77.2; also elsewhere on the board
I_STATUS2_OUT: R65.2; also elsewhere on the board
LOCAL/REMOTE1: R56.1, R68.2; also elsewhere on the board
LOCAL/REMOTE1_OUT: R56.2; also elsewhere on the board
LOCAL/REMOTE2: R62.1, R74.2; also elsewhere on the board
LOCAL/REMOTE2_OUT: R62.2; also elsewhere on the board
TRIP1: R55.1, R67.2; also elsewhere on the board
TRIP1_OUT: R55.2; also elsewhere on the board
TRIP2: R61.1, R73.2; also elsewhere on the board
TRIP2_OUT: R61.2; also elsewhere on the board
V_STATUS1: R58.1, R70.2; also elsewhere on the board
V_STATUS1_OUT: R58.2; also elsewhere on the board
V_STATUS2: R64.1, R76.2; also elsewhere on the board
V_STATUS2_OUT: R64.2; also elsewhere on the board

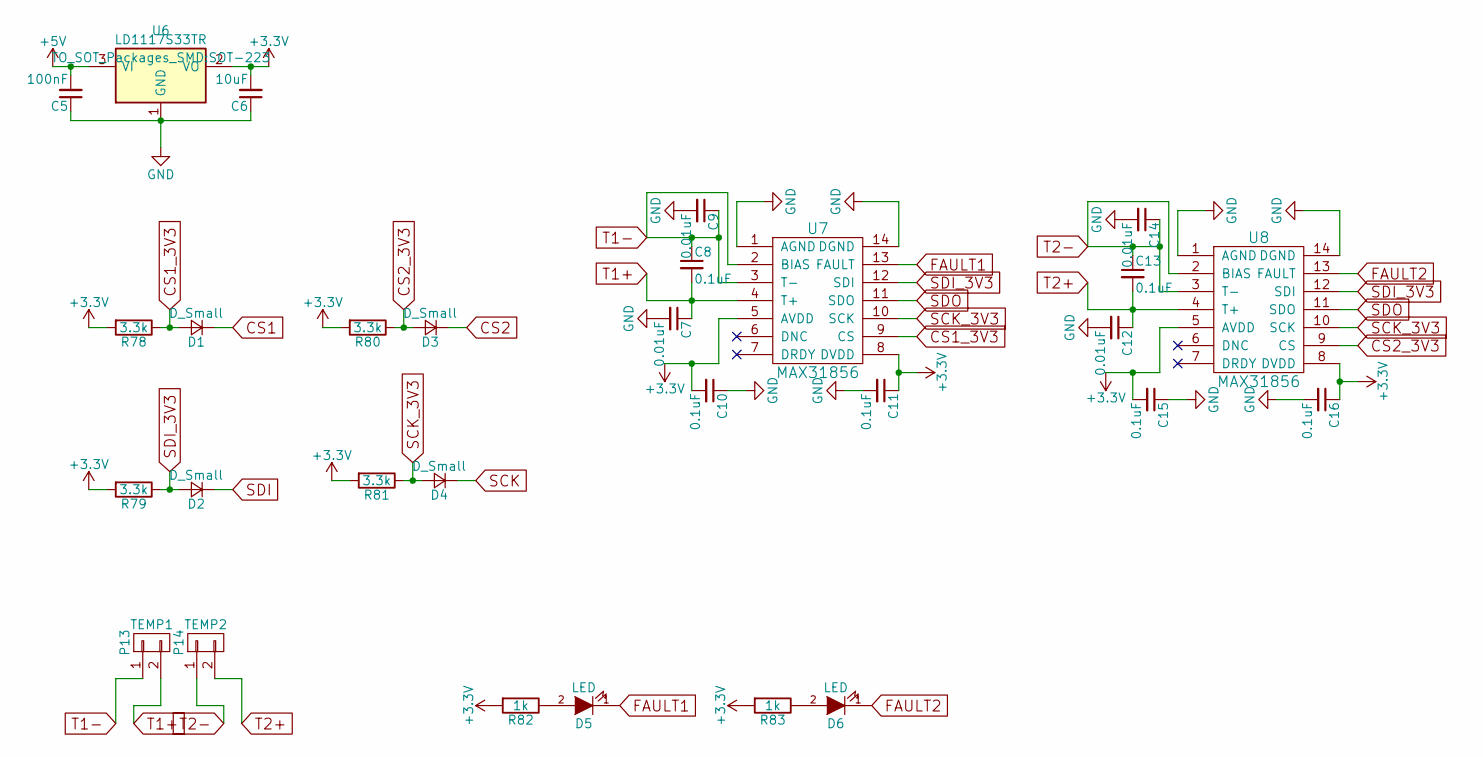
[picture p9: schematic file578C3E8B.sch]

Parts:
C5: 100nF; C_0805
C6: 10uF; C_0805
C7, C9, C12, C14: 0.01uF; C_0805
C8, C10, C11, C13, C15, C16: 0.1uF; C_0805
D1, D2, D3, D4: D_Small; SOD-323
D5, D6: LED; LED-3MM
P13: TEMP1; TerminalBlock_Pheonix_PT-3.5mm_2pol
P14: TEMP2; TerminalBlock_Pheonix_PT-3.5mm_2pol
R78, R79, R80, R81: 3.3k; R_0603
R82, R83: 1k; R_0603
U6: LD1117S33TR; SOT-223
U7, U8: MAX31856; TSSOP-14_4.4x5mm_Pitch0.65mm

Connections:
+3V3: C6.2, C10.2, C11.1, C15.2, C16.1, R78.2, R79.2, R80.2, R81.2, R82.2, R83.2, U6.2 (VO), U7.5 (AVDD), U7.8 (DVDD), U8.5 (AVDD), U8.8 (DVDD)
+5V: C5.2, U6.3 (VI); also elsewhere on the board
CS1: D1.1 (K); also elsewhere on the board
CS1_3V3: D1.2 (A), R78.1, U7.9 (CS)
CS2: D3.1 (K); also elsewhere on the board
CS2_3V3: D3.2 (A), R80.1, U8.9 (CS)
FAULT1: D5.1 (K), U7.13 (FAULT)
FAULT2: D6.1 (K), U8.13 (FAULT)
GND: C5.1, C6.1, C7.2, C9.2, C10.1, C11.2, C12.2, C14.2, C15.1, C16.2, U6.1 (GND), U7.1 (AGND), U7.14 (DGND), U8.1 (AGND), U8.14 (DGND); also elsewhere on the board
unnamed: D5.2 (A), R82.1
unnamed: D6.2 (A), R83.1
SCK: D4.1 (K); also elsewhere on the board
SCK_3V3: D4.2 (A), R81.1, U7.10 (SCK), U8.10 (SCK)
SDI: D2.1 (K); also elsewhere on the board
SDI_3V3: D2.2 (A), R79.1, U7.12 (SDI), U8.12 (SDI)
SDO: U7.11 (SDO), U8.11 (SDO); also elsewhere on the board
T1+: C7.1, C8.2, P13.2, U7.4 (T+)
T1-: C8.1, C9.1, P13.1, U7.2 (BIAS), U7.3 (T-)
T2+: C12.1, C13.2, P14.2, U8.4 (T+)
T2-: C13.1, C14.1, P14.1, U8.2 (BIAS), U8.3 (T-)

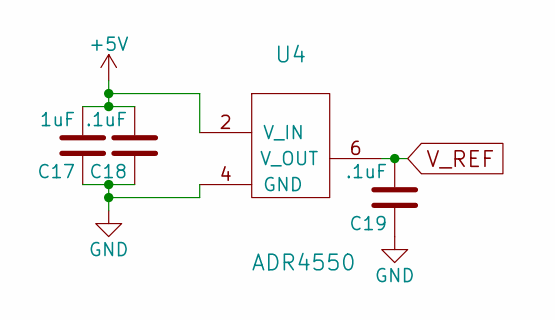
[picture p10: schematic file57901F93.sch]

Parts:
C17: 1uF; C_0805
C18, C19: .1uF; C_0805
U4: ADR4550; SOIC-8_3.9x4.9mm_Pitch1.27mm

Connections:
+5V: C17.2, C18.2, U4.2 (V_IN); also elsewhere on the board
GND: C17.1, C18.1, C19.1, U4.4 (GND); also elsewhere on the board
V_REF: C19.2, U4.6 (V_OUT); also elsewhere on the board

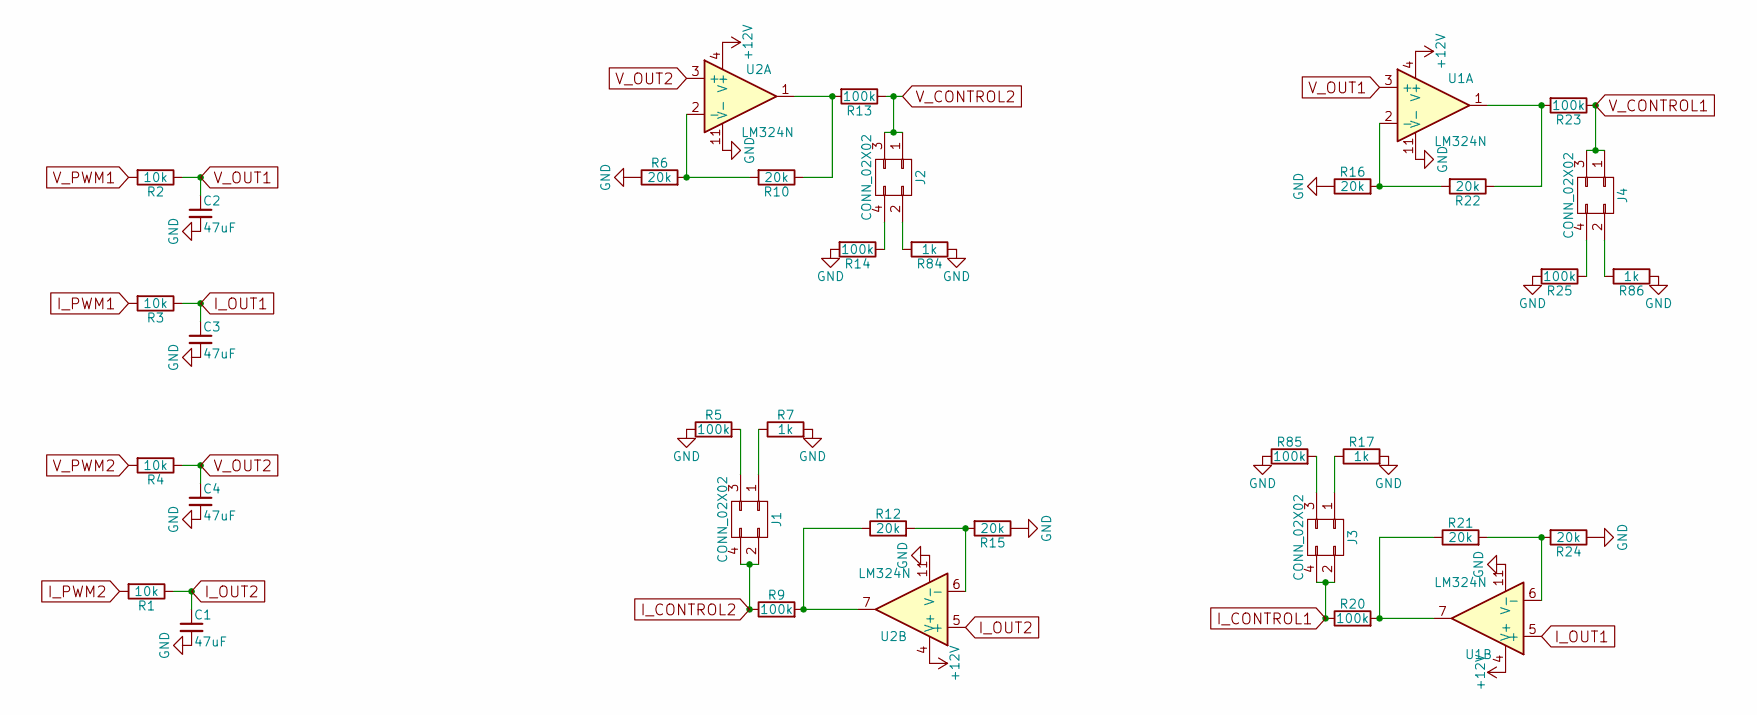
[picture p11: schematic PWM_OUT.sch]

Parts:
C1, C2, C3, C4: 47uF; C_1210
J1, J2, J3, J4: CONN_02X02; Pin_Header_Straight_2x02_Pitch2.54mm
R1, R2, R3, R4: 10k; R_0603
R5, R9, R13, R14, R20, R23, R25, R85: 100k; R_0603
R6, R10, R12, R15, R16, R21, R22, R24: 20k; R_0603
R7, R17, R84, R86: 1k; R_0603
U1, U2: LM324N; SOIC-14_N

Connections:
+12V: U1.4 (V+), U2.4 (V+); also elsewhere on the board
GND: C1.2, C2.2, C3.2, C4.2, R5.1, R6.1, R7.2, R14.2, R15.1, R16.1, R17.2, R24.1, R25.2, R84.1, R85.1, R86.1, U1.11 (V-), U2.11 (V-); also elsewhere on the board
I_CONTROL1: J3.2, J3.4, R20.1; also elsewhere on the board
I_CONTROL2: J1.2, J1.4, R9.1; also elsewhere on the board
I_OUT1: C3.1, R3.1, U1.5 (+)
I_OUT2: C1.1, R1.1, U2.5 (+)
I_PWM1: R3.2; also elsewhere on the board
I_PWM2: R1.2; also elsewhere on the board
unnamed: J1.1, R7.1
unnamed: J1.3, R5.2
unnamed: J2.2, R84.2
unnamed: J2.4, R14.1
unnamed: J3.1, R17.1
unnamed: J3.3, R85.2
unnamed: J4.2, R86.2
unnamed: J4.4, R25.1
unnamed: R10.1, R13.2, U2.1
unnamed: R6.2, R10.2, U2.2 (-)
unnamed: R9.2, R12.1, U2.7
unnamed: R12.2, R15.2, U2.6 (-)
unnamed: R16.2, R22.2, U1.2 (-)
unnamed: R20.2, R21.1, U1.7
unnamed: R21.2, R24.2, U1.6 (-)
unnamed: R22.1, R23.2, U1.1
V_CONTROL1: J4.1, J4.3, R23.1; also elsewhere on the board
V_CONTROL2: J2.1, J2.3, R13.1; also elsewhere on the board
V_OUT1: C2.1, R2.1, U1.3 (+)
V_OUT2: C4.1, R4.1, U2.3 (+)
V_PWM1: R2.2; also elsewhere on the board
V_PWM2: R4.2; also elsewhere on the board

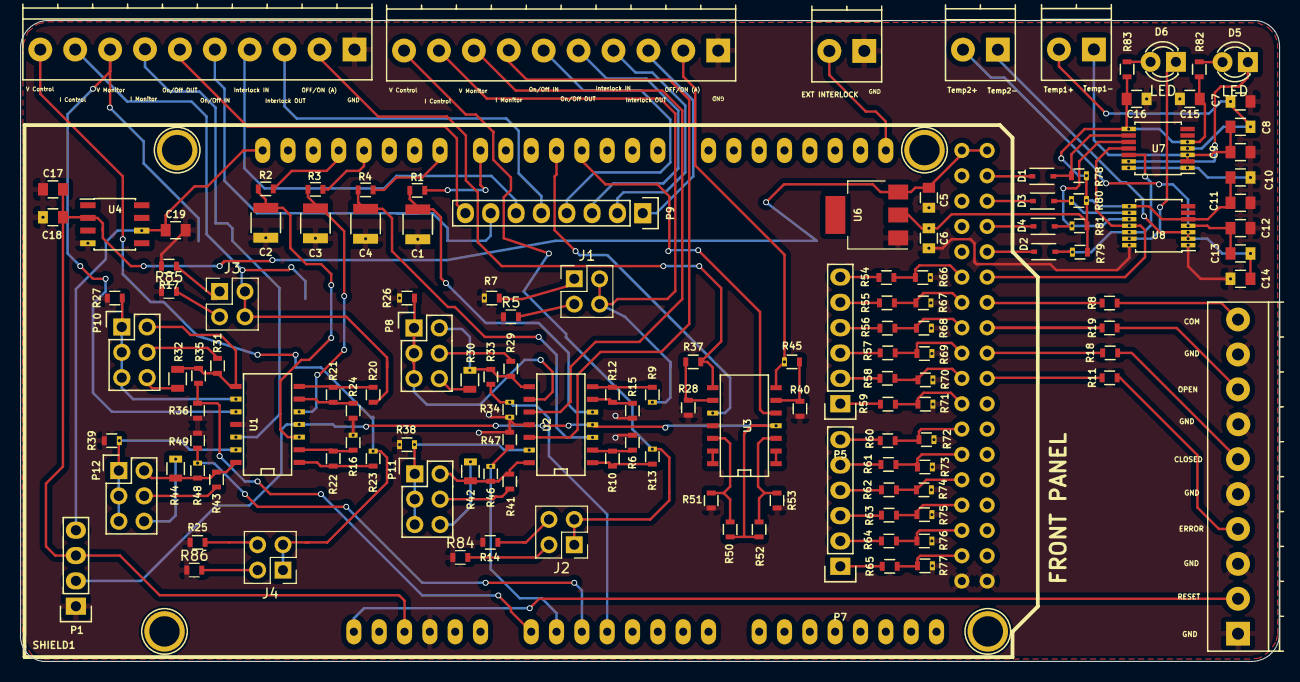
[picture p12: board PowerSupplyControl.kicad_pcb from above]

Board: 2 copper layers, 126.2 x 64.3 mm, 137 parts (0 on the bottom side), 126 nets.

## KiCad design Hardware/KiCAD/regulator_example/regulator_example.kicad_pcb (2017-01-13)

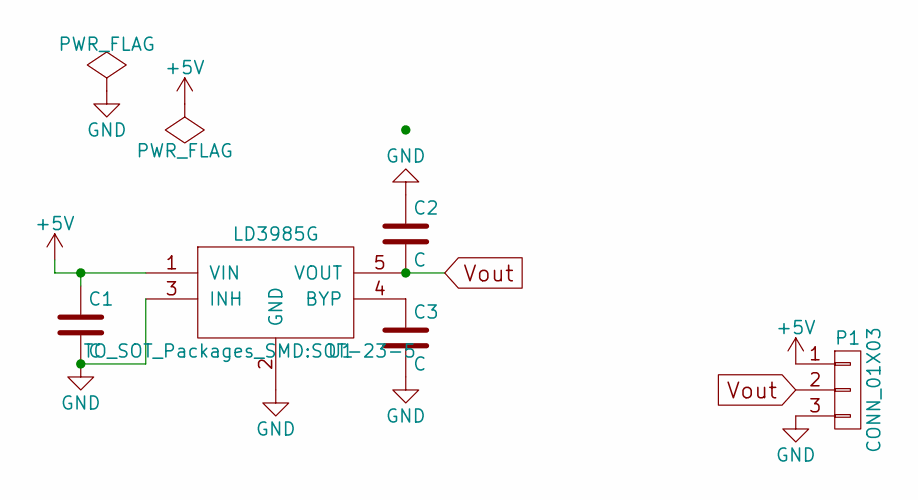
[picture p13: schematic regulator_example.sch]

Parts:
C1, C2, C3: C; C_0805_HandSoldering
P1: CONN_01X03; Pin_Header_Straight_1x03
U1: LD3985G; SOT-23-5

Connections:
+5V: C1.1, P1.1, U1.1 (VIN)
GND: C1.2, C2.1, C3.2, P1.3, U1.2 (GND), U1.3 (INH)
unnamed: C3.1, U1.4 (BYP)
Vout: C2.2, P1.2, U1.5 (VOUT)

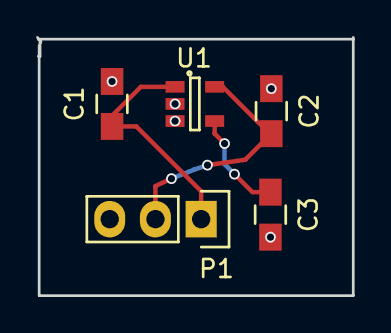
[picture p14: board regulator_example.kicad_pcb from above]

Board: 2 copper layers, 17.6 x 14.4 mm, 5 parts (0 on the bottom side), 4 nets.

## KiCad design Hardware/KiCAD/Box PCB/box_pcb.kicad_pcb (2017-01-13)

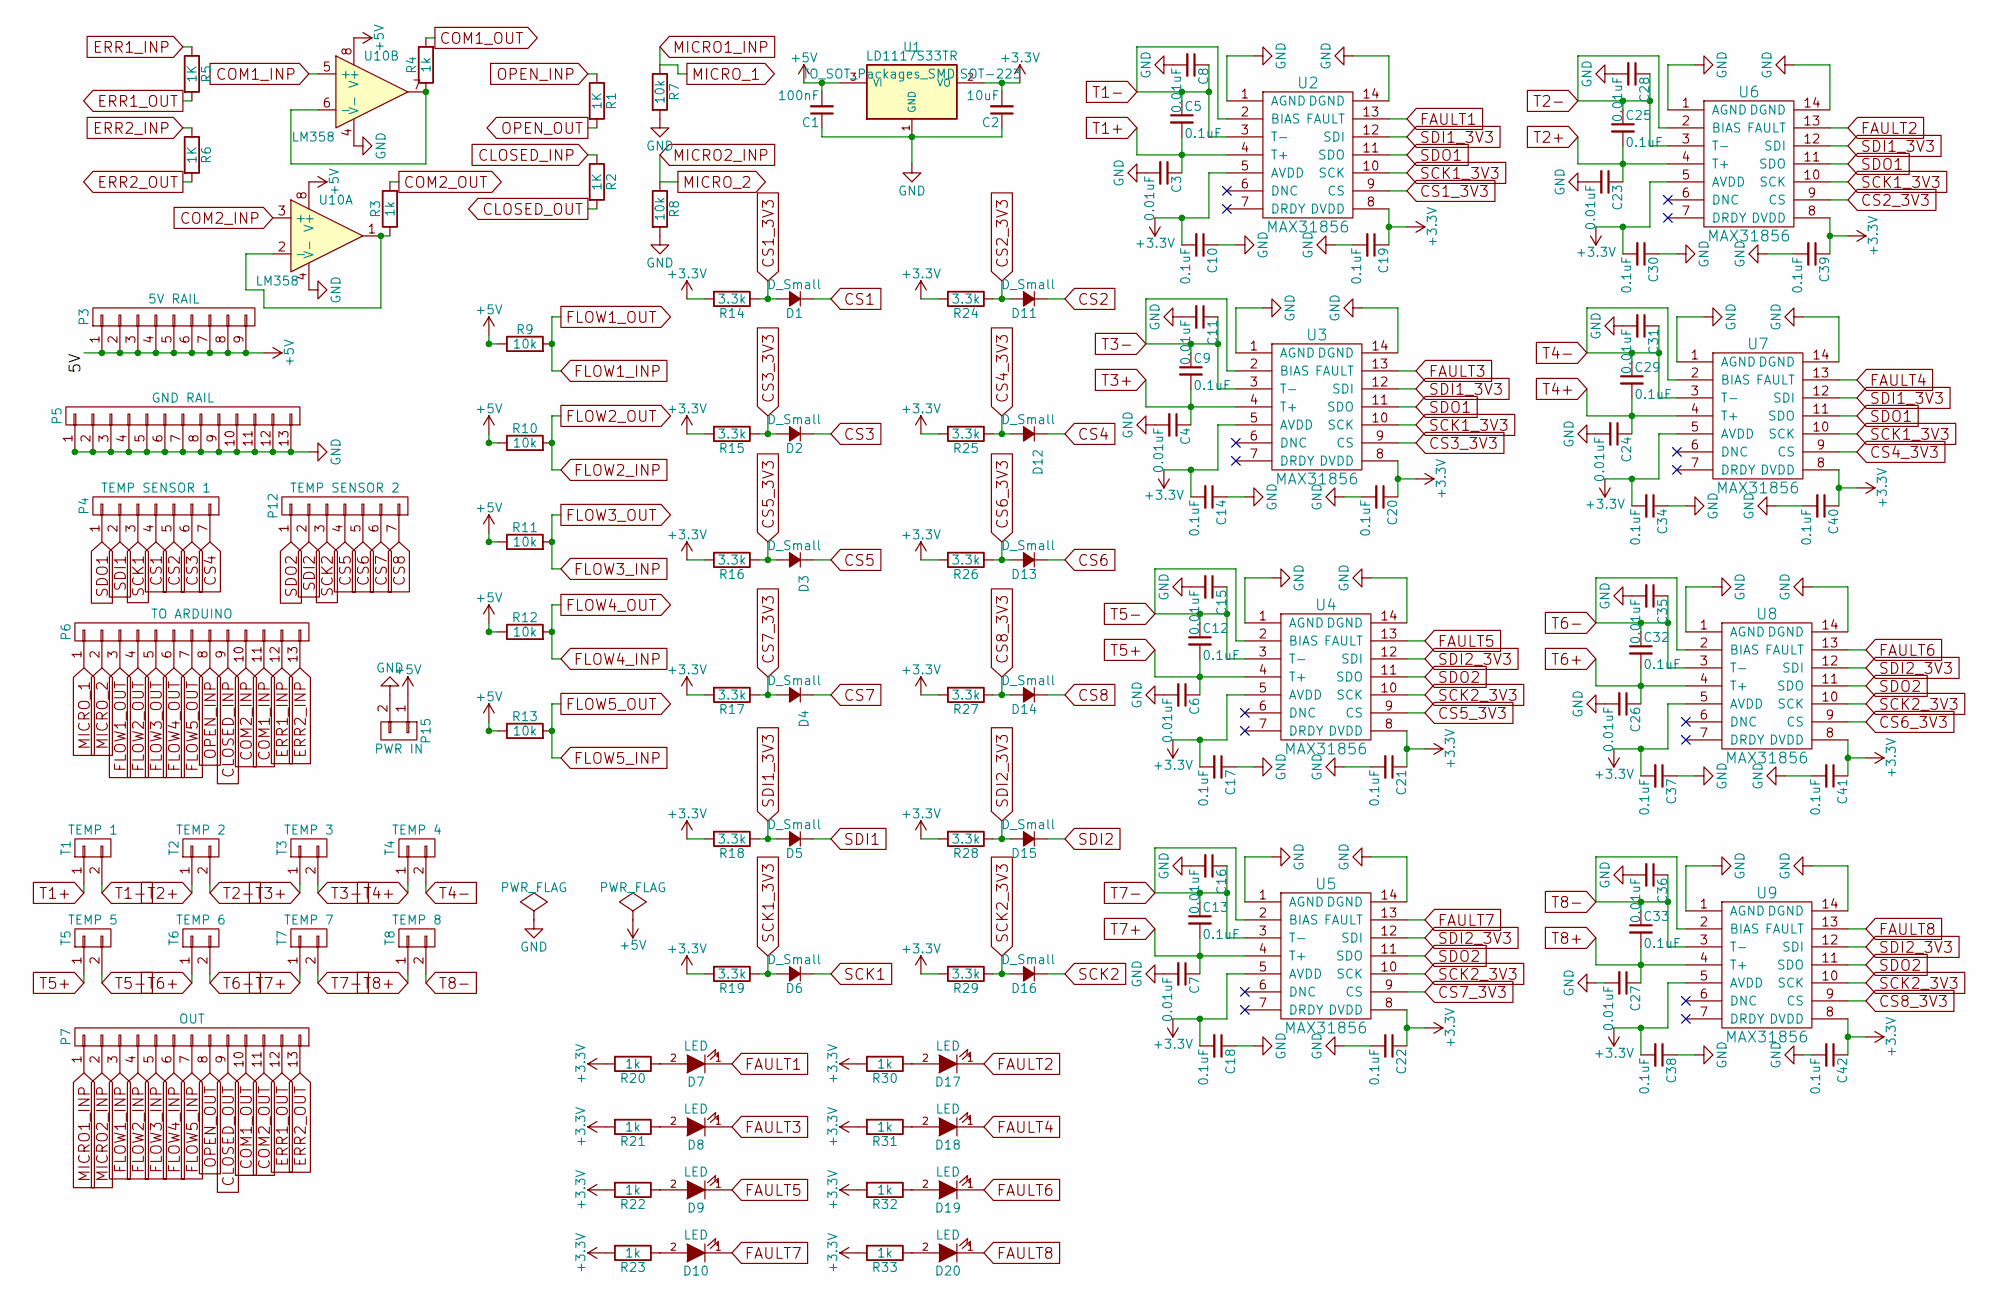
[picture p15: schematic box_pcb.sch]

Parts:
C1: 100nF; C_0805_HandSoldering
C2: 10uF; C_0805_HandSoldering
C3, C4, C6, C7, C8, C11, C15, C16, C23, C24, C26, C27, C28, C31, C35, C36: 0.01uF; C_0805_HandSoldering
C5, C9, C10, C12, C13, C14, C17, C18, C19, C20, C21, C22, C25, C29, C30, C32, C33, C34, C37, C38, C39, C40, C41, C42: 0.1uF; C_0805_HandSoldering
D1, D2, D3, D4, D5, D6, D11, D12, D13, D14, D15, D16: D_Small; SOD-323
D7, D8, D9, D10, D17, D18, D19, D20: LED; LED-3MM
P3: 5V RAIL; Socket_Strip_Straight_1x09
P4: TEMP SENSOR 1; Socket_Strip_Straight_1x07
P5: GND RAIL; Socket_Strip_Straight_1x13
P6: TO ARDUINO; Socket_Strip_Straight_1x13
P7: OUT; Socket_Strip_Straight_1x13
P12: TEMP SENSOR 2; Socket_Strip_Straight_1x07
P15: PWR IN; Socket_Strip_Straight_1x02
R1, R2, R5, R6: 1K; R_0603_HandSoldering
R3, R4, R20, R21, R22, R23, R30, R31, R32, R33: 1k; R_0603_HandSoldering
R7, R8, R9, R10, R11, R12, R13: 10k; R_0603_HandSoldering
R14, R15, R16, R17, R18, R19, R24, R25, R26, R27, R28, R29: 3.3k; R_0603_HandSoldering
T1: TEMP 1; Socket_Strip_Straight_1x02
T2: TEMP 2; Socket_Strip_Straight_1x02
T3: TEMP 3; Socket_Strip_Straight_1x02
T4: TEMP 4; Socket_Strip_Straight_1x02
T5: TEMP 5; Socket_Strip_Straight_1x02
T6: TEMP 6; Socket_Strip_Straight_1x02
T7: TEMP 7; Socket_Strip_Straight_1x02
T8: TEMP 8; Socket_Strip_Straight_1x02
U1: LD1117S33TR; SOT-223
U2, U3, U4, U5, U6, U7, U8, U9: MAX31856; TSSOP-14_4.4x5mm_Pitch0.65mm
U10: LM358; SOIC-8-N

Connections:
+3V3: C2.2, C10.2, C14.2, C17.2, C18.2, C19.1, C20.1, C21.1, C22.1, C30.2, C34.2, C37.2, C38.2, C39.1, C40.1, C41.1, C42.1, R14.2, R15.2, R16.2, R17.2, R18.2, R19.2, R20.2, R21.2, R22.2, R23.2, R24.2, R25.2, R26.2, R27.2, R28.2, R29.2, R30.2, R31.2, R32.2, R33.2, U1.2 (VO), U2.5 (AVDD), U2.8 (DVDD), U3.5 (AVDD), U3.8 (DVDD), U4.5 (AVDD), U4.8 (DVDD), U5.5 (AVDD), U5.8 (DVDD), U6.5 (AVDD), U6.8 (DVDD), U7.5 (AVDD), U7.8 (DVDD), U8.5 (AVDD), U8.8 (DVDD), U9.5 (AVDD), U9.8 (DVDD)
+5V: C1.2, P3.1, P3.2, P3.3, P3.4, P3.5, P3.6, P3.7, P3.8, P3.9, P15.1, R9.1, R10.1, R11.1, R12.1, R13.1, U1.3 (VI), U10.8 (V+)
CLOSED_INP: P6.9, R2.1
CLOSED_OUT: P7.9, R2.2
COM1_INP: P6.11, U10.5 (+)
COM1_OUT: P7.10, R4.2
COM2_INP: P6.10, U10.3 (+)
COM2_OUT: P7.11, R3.2
CS1: D1.1 (K), P4.4
CS1_3V3: D1.2 (A), R14.1, U2.9 (CS)
CS2: D11.1 (K), P4.5
CS2_3V3: D11.2 (A), R24.1, U6.9 (CS)
CS3: D2.1 (K), P4.6
CS3_3V3: D2.2 (A), R15.1, U3.9 (CS)
CS4: D12.1 (K), P4.7
CS4_3V3: D12.2 (A), R25.1, U7.9 (CS)
CS5: D3.1 (K), P12.4
CS5_3V3: D3.2 (A), R16.1, U4.9 (CS)
CS6: D13.1 (K), P12.5
CS6_3V3: D13.2 (A), R26.1, U8.9 (CS)
CS7: D4.1 (K), P12.6
CS7_3V3: D4.2 (A), R17.1, U5.9 (CS)
CS8: D14.1 (K), P12.7
CS8_3V3: D14.2 (A), R27.1, U9.9 (CS)
ERR1_INP: P6.12, R5.1
ERR1_OUT: P7.12, R5.2
ERR2_INP: P6.13, R6.1
ERR2_OUT: P7.13, R6.2
FAULT1: D7.1 (K), U2.13 (FAULT)
FAULT2: D17.1 (K), U6.13 (FAULT)
FAULT3: D8.1 (K), U3.13 (FAULT)
FAULT4: D18.1 (K), U7.13 (FAULT)
FAULT5: D9.1 (K), U4.13 (FAULT)
FAULT6: D19.1 (K), U8.13 (FAULT)
FAULT7: D10.1 (K), U5.13 (FAULT)
FAULT8: D20.1 (K), U9.13 (FAULT)
FLOW1_INP: P6.3, P7.3, R9.2
FLOW2_INP: P6.4, P7.4, R10.2
FLOW3_INP: P6.5, P7.5, R11.2
FLOW4_INP: P6.6, P7.6, R12.2
FLOW5_INP: P6.7, P7.7, R13.2
GND: C1.1, C2.1, C3.2, C4.2, C6.2, C7.2, C8.2, C10.1, C11.2, C14.1, C15.2, C16.2, C17.1, C18.1, C19.2, C20.2, C21.2, C22.2, C23.2, C24.2, C26.2, C27.2, C28.2, C30.1, C31.2, C34.1, C35.2, C36.2, C37.1, C38.1, C39.2, C40.2, C41.2, C42.2, P5.1, P5.2, P5.3, P5.4, P5.5, P5.6, P5.7, P5.8, P5.9, P5.10, P5.11, P5.12, P5.13, P15.2, R7.2, R8.2, U1.1 (GND), U2.1 (AGND), U2.14 (DGND), U3.1 (AGND), U3.14 (DGND), U4.1 (AGND), U4.14 (DGND), U5.1 (AGND), U5.14 (DGND), U6.1 (AGND), U6.14 (DGND), U7.1 (AGND), U7.14 (DGND), U8.1 (AGND), U8.14 (DGND), U9.1 (AGND), U9.14 (DGND), U10.4 (V-)
MICRO1_INP: P6.1, P7.1, R7.1
MICRO2_INP: P6.2, P7.2, R8.1
unnamed: D7.2 (A), R20.1
unnamed: D8.2 (A), R21.1
unnamed: D9.2 (A), R22.1
unnamed: D10.2 (A), R23.1
unnamed: D17.2 (A), R30.1
unnamed: D18.2 (A), R31.1
unnamed: D19.2 (A), R32.1
unnamed: D20.2 (A), R33.1
unnamed: R3.1, U10.1, U10.2 (-)
unnamed: R4.1, U10.6 (-), U10.7
OPEN_INP: P6.8, R1.1
OPEN_OUT: P7.8, R1.2
SCK1: D6.1 (K), P4.3
SCK1_3V3: D6.2 (A), R19.1, U2.10 (SCK), U3.10 (SCK), U6.10 (SCK), U7.10 (SCK)
SCK2: D16.1 (K), P12.3
SCK2_3V3: D16.2 (A), R29.1, U4.10 (SCK), U5.10 (SCK), U8.10 (SCK), U9.10 (SCK)
SDI1: D5.1 (K), P4.2
SDI1_3V3: D5.2 (A), R18.1, U2.12 (SDI), U3.12 (SDI), U6.12 (SDI), U7.12 (SDI)
SDI2: D15.1 (K), P12.2
SDI2_3V3: D15.2 (A), R28.1, U4.12 (SDI), U5.12 (SDI), U8.12 (SDI), U9.12 (SDI)
SDO1: P4.1, U2.11 (SDO), U3.11 (SDO), U6.11 (SDO), U7.11 (SDO)
SDO2: P12.1, U4.11 (SDO), U5.11 (SDO), U8.11 (SDO), U9.11 (SDO)
T1+: C3.1, C5.2, T1.1, U2.4 (T+)
T1-: C5.1, C8.1, T1.2, U2.2 (BIAS), U2.3 (T-)
T2+: C23.1, C25.2, T2.1, U6.4 (T+)
T2-: C25.1, C28.1, T2.2, U6.2 (BIAS), U6.3 (T-)
T3+: C4.1, C9.2, T3.1, U3.4 (T+)
T3-: C9.1, C11.1, T3.2, U3.2 (BIAS), U3.3 (T-)
T4+: C24.1, C29.2, T4.1, U7.4 (T+)
T4-: C29.1, C31.1, T4.2, U7.2 (BIAS), U7.3 (T-)
T5+: C6.1, C12.2, T5.1, U4.4 (T+)
T5-: C12.1, C15.1, T5.2, U4.2 (BIAS), U4.3 (T-)
T6+: C26.1, C32.2, T6.1, U8.4 (T+)
T6-: C32.1, C35.1, T6.2, U8.2 (BIAS), U8.3 (T-)
T7+: C7.1, C13.2, T7.1, U5.4 (T+)
T7-: C13.1, C16.1, T7.2, U5.2 (BIAS), U5.3 (T-)
T8+: C27.1, C33.2, T8.1, U9.4 (T+)
T8-: C33.1, C36.1, T8.2, U9.2 (BIAS), U9.3 (T-)


Board: 2 copper layers, 78.2 x 95.5 mm, 120 parts (0 on the bottom side), 82 nets.

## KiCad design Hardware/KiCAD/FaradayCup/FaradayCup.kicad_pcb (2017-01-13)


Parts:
C1: 1uF; C_0805
C2, C3: .1uF; C_0805
C4, C5, C6, C7: C_Small; C_0805
P1: I INPUT; TerminalBlock_Pheonix_PT-3.5mm_2pol
P2: FRONT PANEL; Pin_Header_Straight_1x06
P3: PWR RAIL; Pin_Header_Straight_1x02
R1, R2, R9, R10, R11, R12, R13, R14, R15, R16, R17, R18, R19, R20, R21, R22, R23, R24, R25, R26, R27, R28, R29, R30, R31, R32, R33: R_Small; R_0603
SHIELD1: ARDUINO_MEGA_SHIELD
U1: ADR4550; SOIC-8_3.9x4.9mm_Pitch1.27mm
U2, U3, U4: LM324N; SOIC-14_3.9x8.7mm_Pitch1.27mm

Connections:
2mA_1: U3.3 (+); also elsewhere on the board
2mA_2: U3.10 (+); also elsewhere on the board
20mA_1: R9.2, U2.3 (+); also elsewhere on the board
20mA_2: R12.2, U2.12 (+); also elsewhere on the board
200mA_1: R11.2, U2.10 (+); also elsewhere on the board
200mA_2: R10.2, U2.5 (+); also elsewhere on the board
200uA_1: U3.5 (+); also elsewhere on the board
200uA_2: U3.12 (+); also elsewhere on the board
+5V: C1.2, C2.2, P3.2, U1.2 (V_IN), U2.4 (V+), U3.4 (V+), U4.4 (V+); also elsewhere on the board
COM: P2.3, SHIELD1.13
CONTROL1: SHIELD1.11; also elsewhere on the board
CONTROL2: SHIELD1.10; also elsewhere on the board
CONTROL3: SHIELD1.9; also elsewhere on the board
CONTROL4: SHIELD1.8; also elsewhere on the board
CONTROL5: SHIELD1.7; also elsewhere on the board
CONTROL6: SHIELD1.6; also elsewhere on the board
CONTROL7: SHIELD1.5; also elsewhere on the board
CONTROL8: SHIELD1.4; also elsewhere on the board
CURRENT1: P1.2; also elsewhere on the board
CURRENT2: P1.1; also elsewhere on the board
ERROR: R33.1, SHIELD1.12
GND: C1.1, C2.1, C3.1, P2.2, P2.4, P2.6, P3.1, R1.1, R2.1, R9.1, R10.1, R11.1, R12.1, R13.1, R14.1, R15.1, R16.1, SHIELD1.GND1, SHIELD1.GND2, SHIELD1.GND3, U1.4 (GND), U2.11 (V-), U3.11 (V-), U4.3 (+), U4.5 (+), U4.10 (+), U4.11 (V-), U4.12 (+); also elsewhere on the board
unnamed: C4.1, R21.1, R25.2, U3.1
unnamed: C4.2, R21.2, U3.2 (-)
unnamed: C5.1, R22.1, R26.2, U3.7
unnamed: C5.2, R22.2, U3.6 (-)
unnamed: C6.1, R23.1, R27.2, U3.8
unnamed: C6.2, R23.2, U3.9 (-)
unnamed: C7.1, R24.1, R28.2, U3.14
unnamed: C7.2, R24.2, U3.13 (-)
unnamed: P2.5, R33.2
unnamed: R13.2, R17.2, U2.2 (-)
unnamed: R14.2, R18.2, U2.6 (-)
unnamed: R15.2, R19.2, U2.9 (-)
unnamed: R16.2, R20.2, U2.13 (-)
unnamed: R25.1, R29.2, U4.2 (-)
unnamed: R26.1, R30.2, U4.6 (-)
unnamed: R27.1, R31.2, U4.9 (-)
unnamed: R28.1, R32.2, U4.13 (-)
READING1: R20.1, U2.14; also elsewhere on the board
READING2: R19.1, U2.8; also elsewhere on the board
READING3: R18.1, U2.7; also elsewhere on the board
READING4: R17.1, U2.1; also elsewhere on the board
READING5: R32.1, U4.14; also elsewhere on the board
READING6: R31.1, U4.8; also elsewhere on the board
READING7: R30.1, U4.7; also elsewhere on the board
READING8: R29.1, U4.1; also elsewhere on the board
RESET: P2.1, SHIELD1.RST
VOLTAGE_1: R1.2, SHIELD1.AD0; also elsewhere on the board
VOLTAGE_2: R2.2, SHIELD1.AD1; also elsewhere on the board
V_REF: C3.2, SHIELD1.AREF, U1.6 (V_OUT)


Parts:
D1, D2, D3, D4, D5, D6, D7, D8: DIODE; SOD-123
Q17, Q18, Q19, Q20, Q21, Q22, Q23, Q24: Q_NPN_BCE; TO-92_Inline_Wide
R35, R36, R37, R38, R39, R40, R42, R43: R_Small; R_0603
RL1, RL2, RL3, RL4, RL5, RL6, RL7, RL8: FINDER-44.62; RELAY

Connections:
2mA_1: RL8.14; also elsewhere on the board
2mA_2: RL4.14; also elsewhere on the board
20mA_1: RL7.24; also elsewhere on the board
20mA_2: RL2.14; also elsewhere on the board
200mA_1: RL3.14; also elsewhere on the board
200mA_2: RL5.14; also elsewhere on the board
200uA_1: RL6.14; also elsewhere on the board
200uA_2: RL1.14; also elsewhere on the board
+5V: D1.1 (K), D2.1 (K), D3.1 (K), D4.1 (K), D5.1 (K), D6.1 (K), D7.1 (K), D8.1 (K), RL1.A1, RL2.A1, RL3.A1, RL4.A1, RL5.A1, RL6.A1, RL7.A1, RL8.A1; also elsewhere on the board
CONTROL1: R36.1; also elsewhere on the board
CONTROL2: R37.1; also elsewhere on the board
CONTROL3: R39.1; also elsewhere on the board
CONTROL4: R42.1; also elsewhere on the board
CONTROL5: R35.1; also elsewhere on the board
CONTROL6: R38.1; also elsewhere on the board
CONTROL7: R40.1; also elsewhere on the board
CONTROL8: R43.1; also elsewhere on the board
CURRENT1: RL2.11, RL3.11, RL5.11, RL7.11; also elsewhere on the board
CURRENT2: RL1.11, RL4.11, RL6.11, RL8.11; also elsewhere on the board
GND: Q17.3 (E), Q18.3 (E), Q19.3 (E), Q20.3 (E), Q21.3 (E), Q22.3 (E), Q23.3 (E), Q24.3 (E); also elsewhere on the board
unnamed: D1.2 (A), Q17.2 (C), RL1.A2
unnamed: D2.2 (A), Q18.2 (C), RL2.A2
unnamed: D3.2 (A), Q19.2 (C), RL3.A2
unnamed: D4.2 (A), Q20.2 (C), RL4.A2
unnamed: D5.2 (A), Q21.2 (C), RL5.A2
unnamed: D6.2 (A), Q22.2 (C), RL6.A2
unnamed: D7.2 (A), Q23.2 (C), RL7.A2
unnamed: D8.2 (A), Q24.2 (C), RL8.A2
unnamed: Q17.1 (B), R35.2
unnamed: Q18.1 (B), R36.2
unnamed: Q19.1 (B), R37.2
unnamed: Q20.1 (B), R38.2
unnamed: Q21.1 (B), R39.2
unnamed: Q22.1 (B), R40.2
unnamed: Q23.1 (B), R42.2
unnamed: Q24.1 (B), R43.2
READING1: RL2.21; also elsewhere on the board
READING2: RL3.21; also elsewhere on the board
READING3: RL5.21; also elsewhere on the board
READING4: RL7.21; also elsewhere on the board
READING5: RL1.21; also elsewhere on the board
READING6: RL4.21; also elsewhere on the board
READING7: RL6.21; also elsewhere on the board
READING8: RL8.21; also elsewhere on the board
VOLTAGE_1: RL3.24, RL6.24, RL7.14, RL8.24; also elsewhere on the board
VOLTAGE_2: RL1.24, RL2.24, RL4.24, RL5.24; also elsewhere on the board


Board: 2 copper layers, 99.1 x 61.0 mm, 74 parts (0 on the bottom side), 67 nets.

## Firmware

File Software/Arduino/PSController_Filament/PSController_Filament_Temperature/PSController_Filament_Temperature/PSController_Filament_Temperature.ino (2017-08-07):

#include <Channel.h>
#include <Communication.h>
#include <MAX31856.h>

// A PS Controller for the Filament Power Supplies 
// * PS1 = Filament Heating (blue big guy on bottom)
// 0-5 V on Voltage control, 0-100 mV on Current Control
// * PS2 = Filament Discharge (small guy on top)
// 0-10 V on Voltage Control, 0-10 V on Current Control 

// Set up serial communication
char inputMessage[128];
mist1::Communication com = mist1::Communication("TestPSController1");

// Temperature Sensors. 2x.
// The power requirement for the board is less than 2mA.  Most microcontrollers can source or sink a lot more
// than that one each I/O pin.  For example, the ATmega328 supports up to 20mA.  So it is possible to power the
// board using I/O pins for power - so you can turn the board on and off (if you want to).
// FAULT and DRDY are not used by the library (see above)
#define SCK 27
#define SDI 29
#define SDO 31
#define CS1 23
#define CS2 25

// MAX31856 Initial settings (see MAX31856.h and the MAX31856 datasheet)
// The default noise filter is 60Hz, suitable for the USA
#define CR0_INIT  (CR0_AUTOMATIC_CONVERSION + CR0_OPEN_CIRCUIT_FAULT_TYPE_K /* + CR0_NOISE_FILTER_50HZ */)
#define CR1_INIT  (CR1_AVERAGE_2_SAMPLES + CR1_THERMOCOUPLE_TYPE_K)
#define MASK_INIT (~(MASK_VOLTAGE_UNDER_OVER_FAULT + MASK_THERMOCOUPLE_OPEN_FAULT))

// Define pins for error state LED, communication LED
#define LED_ERR 39
#define LED_COM 33
#define LED_OPEN 35
#define LED_CLOSED 37

MAX31856 *temperature1;
MAX31856 *temperature2;

// float t[] = {0.0, 0.0};

// Define pins for power supply control voltages
#define PS1_V_OUT 12  // Cave: For Timer1, "2" maps to pin 12
#define PS1_I_OUT 11  // Cave: For Timer1, "1" maps to pin 11
#define PS2_V_OUT 10
#define PS2_I_OUT 9

// Define pins for power supply read voltages
#define PS1_V_IN 0
#define PS1_I_IN 2
#define PS2_V_IN 3
#define PS2_I_IN 1

// Define pins for relays (PS on/off, PS interlock)
#define PS1_ON 14
#define PS1_ILK 15
#define PS2_ON 16
#define PS2_ILK 17

//Define External Interlock Pin
#define EXT_ILK 21

//Define interlock open/closed
#define CLOSED 1
#define OPEN 0

// Set up interlock switch debounce time
long debouncing_time = 150; //Debouncing Time in Milliseconds
volatile unsigned long last_micros;

volatile unsigned int error_state = 0;
volatile unsigned int interlock_state = OPEN;

/*
// function object prototype for setting relay state
typedef struct setRelay {
 // constructor
 setRelay (const uint8_t relay) : relay_ (relay) {}
 // operator ()
 void operator () (int state)
   {
     if (state == 1) {
       digitalWrite(relay_, LOW);
     } else if (state == 0) {
       digitalWrite(relay_, HIGH);
     }
   }  // end of operator ()

 private:    
   uint8_t relay_;
};

setRelay set_relay1 (RELAY1);
setRelay set_relay2 (RELAY2);
setRelay set_relay3 (RELAY3);
setRelay set_relay4 (RELAY4);
*/

float get_t1(){
  // return t[0];
  return temperature1->readThermocouple(CELSIUS);
}

float get_t2(){
  // return t[1];
  return temperature2->readThermocouple(CELSIUS);
}

void set_ps1_on (float state){
  if (state == 1.0) {
    digitalWrite(PS1_ON, LOW);
  } else if (state == 0.0) {
    digitalWrite(PS1_ON, HIGH);
  }
}

void set_ps2_on (float state){
  if (state == 1.0) {
    digitalWrite(PS2_ON, LOW);
  } else if (state == 0.0) {
    digitalWrite(PS2_ON, HIGH);
  }
}

void set_ps1_v (float value){
  value *= 48.2;
  analogWrite(PS1_V_OUT, value);
}

float get_ps1_v (){
  analogRead(PS1_V_IN);
  int sum10 = 0;
  for (int i = 0; i < 10; i++){
    sum10 += analogRead(PS1_V_IN);
  }
  return sum10 / 1605.4;
}

void set_ps2_v (float value){
  value *= 24.1;
  analogWrite(PS2_V_OUT, value);
}

float get_ps2_v (){
  analogRead(PS2_V_IN);
  int sum10 = 0;
  for (int i = 0; i < 10; i++){
    sum10 += analogRead(PS2_V_IN);
  }
  return sum10 / 852.7;
}

void set_ps1_i (float value){
  value *= 48.2;
  analogWrite(PS1_I_OUT, value);
}

float get_ps1_i (){
  analogRead(PS1_I_IN);
  int sum10 = 0;
  for (int i = 0; i < 10; i++){
    sum10 += analogRead(PS1_I_IN);
  }
  return sum10 / 10.0;
}

void set_ps2_i (float value){
  value *= 24.1;
  analogWrite(PS2_I_OUT, value);
}

float get_ps2_i (){
  analogRead(PS2_I_IN);
  int sum10 = 0;
  for (int i = 0; i < 10; i++){
    sum10 += analogRead(PS2_I_IN);
  }
  return sum10 / 852.7;
}

float get_ext_ilk(){
  return (float) interlock_state;
}

void dummySetFunc(float set_value){
  //Serial.println("Called the dummy function!");
}

float dummyGetFunc(){
  //Serial.println("Called the dummy function!");
}

void setup() {
  Serial.begin(115200);

  //delay(10);

  // Set up analog reference
  analogReference(EXTERNAL);
  
  // Define the pins used to communicate with the MAX31856
  temperature1 = new MAX31856(SDI, SDO, CS1, SCK);
  temperature2 = new MAX31856(SDI, SDO, CS2, SCK);
  
  // Initializing the MAX31855's registers
  temperature1->writeRegister(REGISTER_CR0, CR0_INIT);
  temperature1->writeRegister(REGISTER_CR1, CR1_INIT);
  temperature1->writeRegister(REGISTER_MASK, MASK_INIT);

  temperature2->writeRegister(REGISTER_CR0, CR0_INIT);
  temperature2->writeRegister(REGISTER_CR1, CR1_INIT);
  temperature2->writeRegister(REGISTER_MASK, MASK_INIT);

  // Initialize Com and Error LED's
  pinMode(LED_ERR, OUTPUT);
  pinMode(LED_COM, OUTPUT);
  pinMode(LED_OPEN, OUTPUT);
  pinMode(LED_CLOSED, OUTPUT);
  
  digitalWrite(LED_COM, LOW);
  digitalWrite(LED_ERR, LOW);
  digitalWrite(LED_OPEN, LOW);
  digitalWrite(LED_CLOSED, LOW);

  // Init V and I output PWM's
  pinMode(PS1_V_OUT, OUTPUT);
  pinMode(PS1_I_OUT, OUTPUT);
  pinMode(PS2_V_OUT, OUTPUT);
  pinMode(PS2_I_OUT, OUTPUT);

  // Set them to 0 V
  digitalWrite(PS1_V_OUT, LOW);
  digitalWrite(PS1_I_OUT, LOW);
  digitalWrite(PS2_V_OUT, LOW);
  digitalWrite(PS2_I_OUT, LOW);

  // Init Relay pins
  pinMode(PS1_ON, OUTPUT);
  pinMode(PS2_ON, OUTPUT);
  pinMode(PS1_ILK, OUTPUT);
  pinMode(PS2_ILK, OUTPUT);

  // Set them all to OFF (pulled HIGH)
  digitalWrite(PS1_ON, HIGH);
  digitalWrite(PS2_ON, HIGH);
  digitalWrite(PS1_ILK, HIGH);
  digitalWrite(PS2_ILK, HIGH);

  // Init External Interlock Pin
  pinMode(EXT_ILK, INPUT);

  com.add_channel(mist1::Channel("TEMP1", 't', 1, &dummySetFunc, &get_t1));
  com.add_channel(mist1::Channel("TEMP2", 't', 2, &dummySetFunc, &get_t2));
  com.add_channel(mist1::Channel("FIL_CUR_ON", 'o', 1, &set_ps1_on, &dummyGetFunc));
  com.add_channel(mist1::Channel("FIL_DCHRG_ON", 'o', 2, &set_ps2_on, &dummyGetFunc));
  com.add_channel(mist1::Channel("FIL_CUR_V", 'v', 1, &set_ps1_v, &get_ps1_v));
  com.add_channel(mist1::Channel("FIL_DCHRG_V", 'v', 2, &set_ps2_v, &get_ps2_v));
  com.add_channel(mist1::Channel("FIL_CUR_I", 'i', 1, &set_ps1_i, &get_ps1_i));
  com.add_channel(mist1::Channel("FIL_DCHRG_I", 'i', 2, &set_ps2_i, &get_ps2_i));
  com.add_channel(mist1::Channel("EXT_ILK", 'x', 1, &dummySetFunc, &get_ext_ilk));  //To read interlock status
  
}

void loop() {
  // Read out temperature sensors
  // t[0] = temperature1->readThermocouple(CELSIUS);
  // t[1] = temperature2->readThermocouple(CELSIUS);

  if (digitalRead(EXT_ILK) == HIGH){
    digitalWrite(PS1_ILK, HIGH);
    digitalWrite(PS2_ILK, HIGH);
    digitalWrite(LED_CLOSED, LOW);
    digitalWrite(LED_OPEN, HIGH);
    interlock_state = OPEN;
  } else {
    digitalWrite(PS1_ILK, LOW);
    digitalWrite(PS2_ILK, LOW);
    digitalWrite(LED_CLOSED, HIGH);
    digitalWrite(LED_OPEN, LOW);
    interlock_state = CLOSED;
  }

  // GUI Communication.
  digitalWrite(LED_COM, LOW);

  if (Serial.available()) {
    
    digitalWrite(LED_COM, HIGH);
    
    com.respond_to_input_message();

  }  
}

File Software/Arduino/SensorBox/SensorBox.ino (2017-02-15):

#include <Channel.h>
#include <Communication.h>

// Set up serial communication
char inputMessage[128];
mist1::Communication com = mist1::Communication("Sensor Box");

#include <MAX31856.h>

// Flow meters. x5.
const int flowSensorPins[] = {18, 19, 20, 3, 2};
volatile int flowSensorFreqs[] = {0, 0, 0, 0, 0};
float flowSensorFreqsWrite[] = {0.0, 0.0, 0.0, 0.0, 0.0};
unsigned long currentTime;
unsigned long cloopTime;

// Temperature Sensors. 8x.
// The power requirement for the board is less than 2mA.  Most microcontrollers can source or sink a lot more
// than that one each I/O pin.  For example, the ATmega328 supports up to 20mA.  So it is possible to power the
// board using I/O pins for power - so you can turn the board on and off (if you want to).
// FAULT and DRDY are not used by the library (see above)
#define SCK1    44
#define SDI1    42
#define SDO1    40

#define SCK2    49
#define SDI2    51
#define SDO2    53

#define CS1    46
#define CS2    48
#define CS3    50
#define CS4    52
#define CS5    47
#define CS6    45
#define CS7    43
#define CS8    41

// Define pins for error state LED, communication LED
#define LED_ERR 12
#define LED_COM 13

// MAX31856 Initial settings (see MAX31856.h and the MAX31856 datasheet)
// The default noise filter is 60Hz, suitable for the USA
#define CR0_INIT  (CR0_AUTOMATIC_CONVERSION + CR0_OPEN_CIRCUIT_FAULT_TYPE_K /* + CR0_NOISE_FILTER_50HZ */)
#define CR1_INIT  (CR1_AVERAGE_2_SAMPLES + CR1_THERMOCOUPLE_TYPE_K)
#define MASK_INIT (~(MASK_VOLTAGE_UNDER_OVER_FAULT + MASK_THERMOCOUPLE_OPEN_FAULT))

MAX31856 *temperature1;
MAX31856 *temperature2;
MAX31856 *temperature3;
MAX31856 *temperature4;
MAX31856 *temperature5;
MAX31856 *temperature6;
MAX31856 *temperature7;
//MAX31856 *temperature8;

float t[] = {0.0, 0.0, 0.0, 0.0, 0.0, 0.0, 0.0, 0.0};


float get_t1(){
  return t[0];
}

float get_t2(){
  return t[1];
}

float get_t3(){
  return t[2];
}

float get_t4(){
  return t[3];
}

float get_t5(){
  return t[4];
}

float get_t6(){
  return t[5];
}

float get_t7(){
  return t[6];
}

float get_flow1(){
  return flowSensorFreqsWrite[0];
}

float get_flow2(){
  return flowSensorFreqsWrite[1];
}

float get_flow3(){
  return flowSensorFreqsWrite[2];
}

float get_flow4(){
  return flowSensorFreqsWrite[3];
}

float get_flow5(){
  return flowSensorFreqsWrite[4];
}

void dummyFunc(float set_value){
  //Serial.println("Called the dummy function!");
}

void setup()   { 
  // Init Com and Error LED's
  pinMode(LED_ERR, OUTPUT);
  pinMode(LED_COM, OUTPUT);
  digitalWrite(LED_COM, LOW);
  digitalWrite(LED_ERR, LOW);
  
  // Flow Meters.
  for (unsigned i = 0; i < sizeof(flowSensorPins) / sizeof(int); i++) {
    pinMode(flowSensorPins[i], INPUT);
    // Activate the pullup resistor
    digitalWrite(flowSensorPins[i], HIGH);
  }

  Serial.begin(115200); // 115200

  // Interrupts for flow sensors.
  attachInterrupt(digitalPinToInterrupt(flowSensorPins[0]), flow_interrupt0, RISING);
  attachInterrupt(digitalPinToInterrupt(flowSensorPins[1]), flow_interrupt1, RISING);
  attachInterrupt(digitalPinToInterrupt(flowSensorPins[2]), flow_interrupt2, RISING);
  attachInterrupt(digitalPinToInterrupt(flowSensorPins[3]), flow_interrupt3, RISING);
  attachInterrupt(digitalPinToInterrupt(flowSensorPins[4]), flow_interrupt4, RISING);

  // Define the pins used to communicate with the MAX31856
  temperature1 = new MAX31856(SDI1, SDO1, CS1, SCK1);
  temperature2 = new MAX31856(SDI1, SDO1, CS2, SCK1);
  temperature3 = new MAX31856(SDI1, SDO1, CS3, SCK1);
  temperature4 = new MAX31856(SDI1, SDO1, CS4, SCK1);
  temperature5 = new MAX31856(SDI2, SDO2, CS5, SCK2);
  temperature6 = new MAX31856(SDI2, SDO2, CS6, SCK2);
  temperature7 = new MAX31856(SDI2, SDO2, CS7, SCK2);
//  temperature8 = new MAX31856(SDI2, SDO2, CS8, SCK2);
  
  // Initializing the MAX31855's registers
  temperature1->writeRegister(REGISTER_CR0, CR0_INIT);
  temperature1->writeRegister(REGISTER_CR1, CR1_INIT);
  temperature1->writeRegister(REGISTER_MASK, MASK_INIT);

  temperature2->writeRegister(REGISTER_CR0, CR0_INIT);
  temperature2->writeRegister(REGISTER_CR1, CR1_INIT);
  temperature2->writeRegister(REGISTER_MASK, MASK_INIT);

  temperature3->writeRegister(REGISTER_CR0, CR0_INIT);
  temperature3->writeRegister(REGISTER_CR1, CR1_INIT);
  temperature3->writeRegister(REGISTER_MASK, MASK_INIT);

  temperature4->writeRegister(REGISTER_CR0, CR0_INIT);
  temperature4->writeRegister(REGISTER_CR1, CR1_INIT);
  temperature4->writeRegister(REGISTER_MASK, MASK_INIT);

  temperature5->writeRegister(REGISTER_CR0, CR0_INIT);
  temperature5->writeRegister(REGISTER_CR1, CR1_INIT);
  temperature5->writeRegister(REGISTER_MASK, MASK_INIT);

  temperature6->writeRegister(REGISTER_CR0, CR0_INIT);
  temperature6->writeRegister(REGISTER_CR1, CR1_INIT);
  temperature6->writeRegister(REGISTER_MASK, MASK_INIT);

  temperature7->writeRegister(REGISTER_CR0, CR0_INIT);
  temperature7->writeRegister(REGISTER_CR1, CR1_INIT);
  temperature7->writeRegister(REGISTER_MASK, MASK_INIT);

//  temperature8->writeRegister(REGISTER_CR0, CR0_INIT);
//  temperature8->writeRegister(REGISTER_CR1, CR1_INIT);
//  temperature8->writeRegister(REGISTER_MASK, MASK_INIT);

  com.add_channel(mist1::Channel("TEMP1", 't', 1, &dummyFunc, &get_t1));
  com.add_channel(mist1::Channel("TEMP2", 't', 2, &dummyFunc, &get_t2));
  com.add_channel(mist1::Channel("TEMP3", 't', 3, &dummyFunc, &get_t3));
  com.add_channel(mist1::Channel("TEMP4", 't', 4, &dummyFunc, &get_t4));
  com.add_channel(mist1::Channel("TEMP5", 't', 5, &dummyFunc, &get_t5));
  com.add_channel(mist1::Channel("TEMP6", 't', 6, &dummyFunc, &get_t6));
  com.add_channel(mist1::Channel("TEMP7", 't', 7, &dummyFunc, &get_t7));

  com.add_channel(mist1::Channel("FLOW1", 'f', 1, &dummyFunc, &get_flow1));
  com.add_channel(mist1::Channel("FLOW2", 'f', 2, &dummyFunc, &get_flow2));
  com.add_channel(mist1::Channel("FLOW3", 'f', 3, &dummyFunc, &get_flow3));
  com.add_channel(mist1::Channel("FLOW4", 'f', 4, &dummyFunc, &get_flow4));
  com.add_channel(mist1::Channel("FLOW5", 'f', 5, &dummyFunc, &get_flow5));
}

void flow_interrupt0() {
  flowSensorFreqs[0]++;
}

void flow_interrupt1() {
  flowSensorFreqs[1]++;
}

void flow_interrupt2() {
  flowSensorFreqs[2]++;
}

void flow_interrupt3() {
  flowSensorFreqs[3]++;
}

void flow_interrupt4() {
  flowSensorFreqs[4]++;
}
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

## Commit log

2016-05-31 Read in values from arduino
2016-05-31 Arduino code cleanup
2016-06-01 Separate Interlock System into two devices
2016-06-02 Revamp: move device detials from Handler to Device / Channel
2016-06-06 Only the main thread updates the GUI
2016-06-06 Arduino code => Arrays
2016-06-10 Device locks when corresponding arduino is unplugged and unlocks when it's plugged back in.
2016-06-20 Device add multiple widget fix
2016-06-20 Select which devices to save.
2016-06-21 Add channel / device manually
2016-06-22 Add / Edit device / channel
2016-06-27 Adding devices adds the device to tree view too
2016-07-27 Arduino communication char array
2016-07-28 Arduino number format
2016-07-28 Server code to send / parse messages to arduino
2016-08-02 server mrver messages
    [ID_Overview.xlsx]
2016-08-16 server pool port open one per device
2016-12-08 Arduino com library
2017-01-11 New Arduino code
2017-01-12 Moved old arduino code
    [ID_Overview.xlsx]
2017-01-13 hardware and documents included
    [FaradayCup.kicad_pcb, FaradayCup.sch, IonGaugeController.kicad_pcb, IonGaugeController.sch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]
2017-01-18 Server responds to query messages- change needed because of changes to Arduino code
2017-01-18 Server handles error messages from the Arduino
2017-01-24 Dummy server works ~18Hz
2017-01-25 ThreadPool no longer specifies no. of threads to use- so uses one per each item in the iterator
2017-01-30 temp fix for polling rate display. -DW
    [Power Supplies_phase2.xlsx, PowerSupplyControl-B.SilkS.gbo]
2017-01-31 Moved ThreadPool to global, increased polling rate to 80 Hz. Fixed rounding to full seconds in DummyServer to get nice sine wave. -DW
2017-01-31 reverted and changed a few details in DummyServer. always use /kill so threads are properly terminated. Noticed that we can stably go above 40 Hz after reboot of PC, but drops down after a while (~10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
2017-02-01 DummyServer uses Device Drivers now
2017-02-02 changed arduino/ to device/ again -DW
2017-02-02 process/thread implementation for query -DW
2017-02-03 Added thread for setting values on the arduino. Response from DummyServer is empty string? -DW
2017-02-03 Added global polling rate and disabled device polling rate until we implement getting it from server. -DW
2017-02-08 Added the modified / debugged server code to RasPiServer/
    [Power Supplies_phase2.xlsx]
2017-02-09 added modified IonGaugeController Arduino code. Only read back pressure as of now. -DW
2017-02-15 Rewrote the RasPi server, more lightweight, now uses a process to keep ports/device ID's updated. Needs to be able to look for MFC at serial port. Do that over at PSFC where I can connect the MFC. -DW
2017-02-15 Intermediate stage of rewriting the server. For reference only, DO NOT USE. -DW
2017-02-15 Arduino changes. Mainly I reduced the delay in getting serial data from 5 ms to 100 us to get better polling rate. -DW
2017-02-20 Added Arduino code for the specific PS controllers (HV and Filament), set up the GUI to run these at PSFC. -DW
2017-02-20 Started implementing the MFC device. -DW
2017-02-22 Fixed having read/write channels ("both"), improved my previous fix for RS485 and separate baud rates. -DW
    [PowerSupplyControl.sch]
2017-02-23 Added temp sensors to Filament PS Controller Arduino software. -DW
2017-08-18 fixed server bug, gui doesn't crash when device unplugged
2017-08-20 Working on device page
2017-08-29 quick fix to check for extension when saving devices
2017-08-30 removed a print statement -DW
2017-08-30 revised device/channel editing
2017-09-01 fixed a few bugs, window close button now kills threads
2017-09-10 preparing to delete devices/channels
2017-09-11 reorder devices on overview
2017-09-11 added saving splitter settings, removed prints, only one warning
2017-09-11 can now delete devices/channels
2017-09-15 added custom widget for device/channel selection
2017-09-15 added teensy pinout
2017-10-16 device timeout and retrying prototype
2017-10-18 move device widget into separate class
2017-10-18 timeout counters for error devices working
2017-10-18 device retry creates only one thread instead of two
2017-11-06 working on kicad now
    [PWM_OUT.sch, PowerSupplyControl-B.Cu.gbl, PowerSupplyControl-B.Mask.gbs, PowerSupplyControl-B.SilkS.gbo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]
2017-11-08 device retry timers are synced to global 30 seconds
2017-11-16 working on temp sensors
    [TemperatureSensor.sch, _saved_file578C3E8B.sch]
2017-11-21 latest cs bug fixes and kicad
    [TemperatureSensor.sch, _saved_TemperatureSensor.sch, _saved_file578C3E8B.sch, _saved_tempsensors.sch]
2017-12-13 scanner daq, temp sensor update
2017-12-13 test ltest layouayout
    [TemperatureSensor.kicad_pcb, TemperatureSensor.sch]
2017-12-13 added gerber files
    [TemperatureSensor-B.Cu.gbr, TemperatureSensor-B.Mask.gbr, TemperatureSensor-B.SilkS.gbr, TemperatureSensor-Edge.Cuts.gbr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]
2017-12-13 updated pico programs
    [TemperatureSensor.kicad_pcb]
2018-01-10 Added stepper motor documentation and drivers
2018-01-11 added drill file
    [TemperatureSensor.drl]
2018-01-29 starting stepper motor controller class
2018-02-16 Added Teensy code for ion gauge controller -DW
    [DigiKey-PartsList.xlsx]
2018-02-22 updating temperature sensor part list & software
    [DigiKey-PartsList.xlsx]
2018-02-22 updated parts list with arduino-compatible barrel jack
    [DigiKey-PartsList.xlsx]
2018-03-23 Teensy based ion gauge controller and Matsusada CO documentation added -DW
2018-03-26 added temp sensor v2 project files, fix control system entry form bug
    [DigiKey-PartsList.xlsx, TemperatureSensor.dsn, TemperatureSensor_v2.kicad_pcb, TemperatureSensor_v2.sch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]
2018-04-09 working on async raspi server
    [temp_sensor_back_plate.ipt, temp_sensor_front_plate.dwg, temp_sensor_front_plate.ipt]
2018-04-09 fix server hang on thread start bug
2018-04-09 small fix to underscore device ids
2018-04-09 add per-device polling rates
2018-04-10 async device polling works pretty well now (serial & ftdi)
